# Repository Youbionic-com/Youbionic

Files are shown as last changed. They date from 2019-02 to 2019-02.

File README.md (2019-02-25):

## Youbionic

Youbionic! Youbionic

## Table of Contents
- [About Us](#about-us)
- [3d Model Assembly](#3d-model-assembly)
- [3d Printing](#3d-printing)
- [Actuators](#actuators)
- [Arduino Code](#arduino-code)
- [Youbionic Hand Handbook - Assembly Instructions](#handbook-assembly-instructions)
- [Technical Drawing](#technical-drawing)
- [Wiring Diagrams](#wiring-diagrams)

## About Us
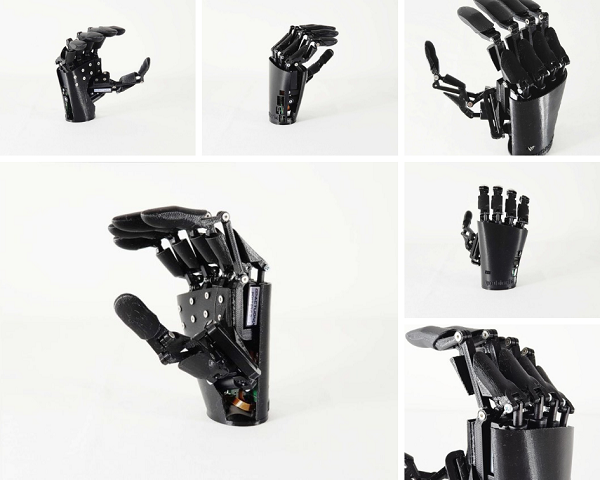
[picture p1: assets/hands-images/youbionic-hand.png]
Youbionic Hand! Youbionic Hand


<a href="http://www.youtube.com/watch?feature=player_embedded&v=_5nRUtHUUb4
" target="_blank">Youbionic Hand 2019</a>

To Understand more about Youbionic Hand, visit our webiste [youbionic.com](https://www.youbionic.com/)

### 3d Model Assembly
[Click here](assets/3d-model-assembly/Youbionic-Hand-2019-Assembly.igs) to find about our Youbionic Hand Assembly related information

### 3d Printing
Click on the below names to View 3D Printing Diagram

- [Back Smooth Logo Left](assets/3d-printing/Back_Smooth_logo_Left.stl) 
- [Back Smooth Logo Right](assets/3d-printing/Back_Smooth_logo_Right.stl)
- [Index Middle Ring](assets/3d-printing/Index-Middle-Ring.stl)
- [Palm Left](assets/3d-printing/Palm_Left.stl)
- [Palm Right](assets/3d-printing/Palm_Right.stl)
- [Rotation Thumb Left](assets/3d-printing/Rotation_Thumb_Left.stl)
- [Rotation Thumb Right](assets/3d-printing/Rotation_Thumb_Right.stl)
- [Thumb Pinkie](assets/3d-printing/Thumb-Pinkie.stl) 

### Actuators
<object data="assets/actuators/Actuonix-PQ12-Datasheet-D.pdf" type="application/pdf" width="700px" height="700px">
    <embed src="assets/actuators/Actuonix-PQ12-Datasheet-D.pdf">
        <p><a href="assets/actuators/Actuonix-PQ12-Datasheet-D.pdf">View PDF</a> to find more about Actuonix PQ12 Datasheet </p>
    </embed>
</object>

### Arduino Code
[Click here](assets/arduino-code/Youbionic_Hand.ino) to find about our Youbionic Hand

### Youbionic Hand Handbook - Assembly Instructions
<object data="assets/handbook-assembly-instructions/Youbionic-Hand-Handbook-Assembly-Instructions.pdf" type="application/pdf" width="700px" height="700px">
    <embed src="assets/handbook-assembly-instructions/Youbionic-Hand-Handbook-Assembly-Instructions.pdf">
        <p><a href="assets/handbook-assembly-instructions/Youbionic-Hand-Handbook-Assembly-Instructions.pdf">View PDF</a> to find more about our Youbionic Hand Handbook Assembly Instructions.</p>
    </embed>
</object>

### Technical Drawing
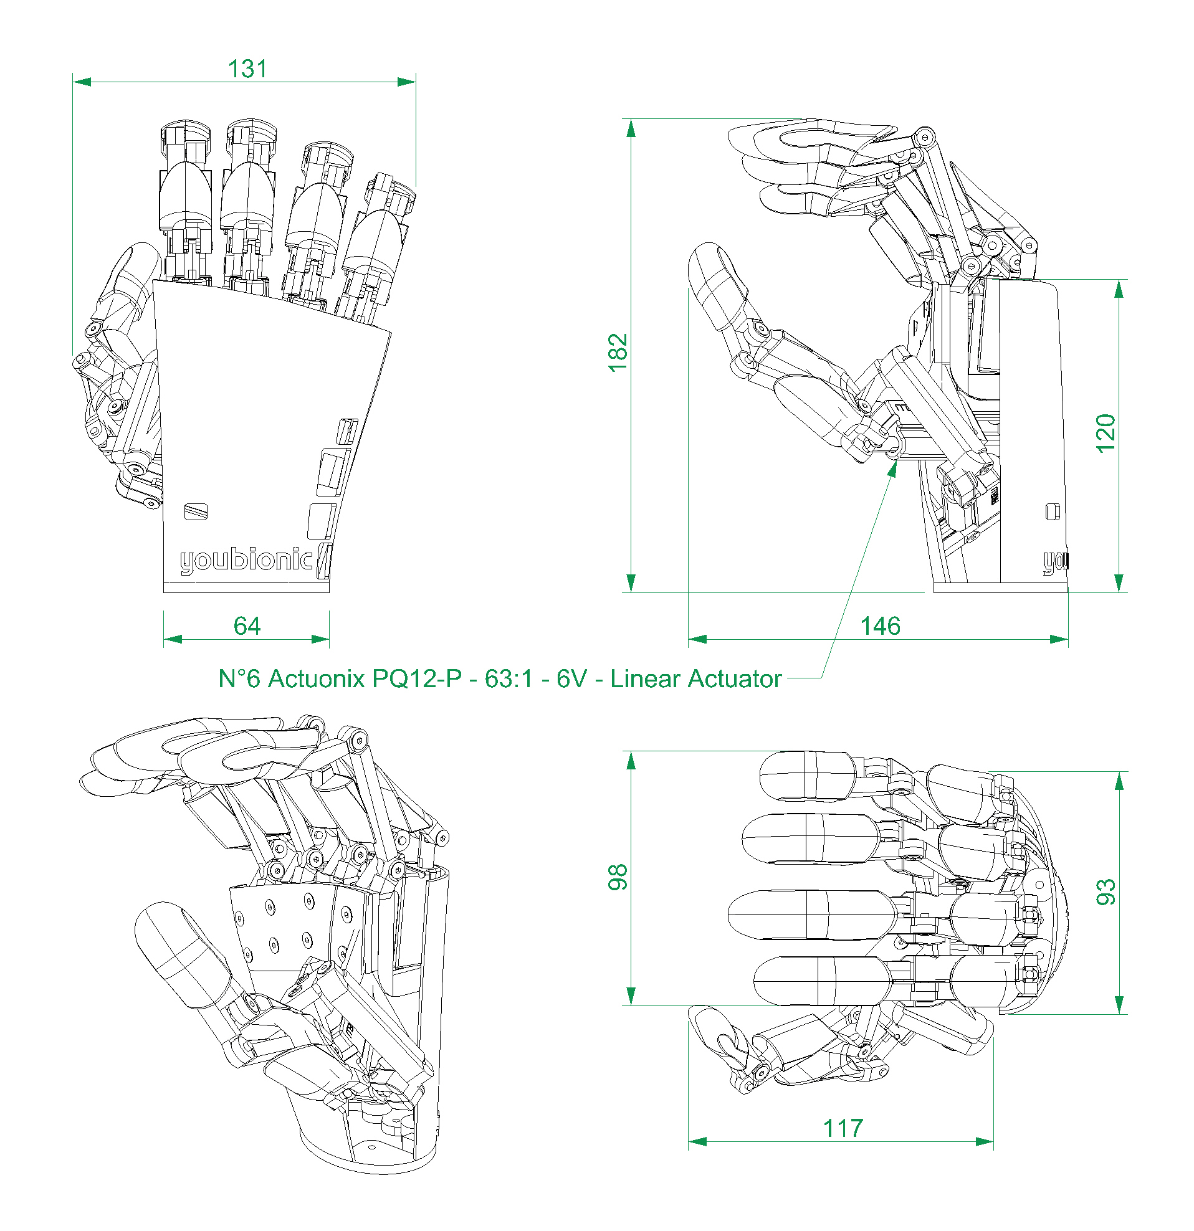
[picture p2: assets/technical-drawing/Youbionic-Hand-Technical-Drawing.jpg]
Technical Drawing! Technical Drawing


### Wiring Diagrams
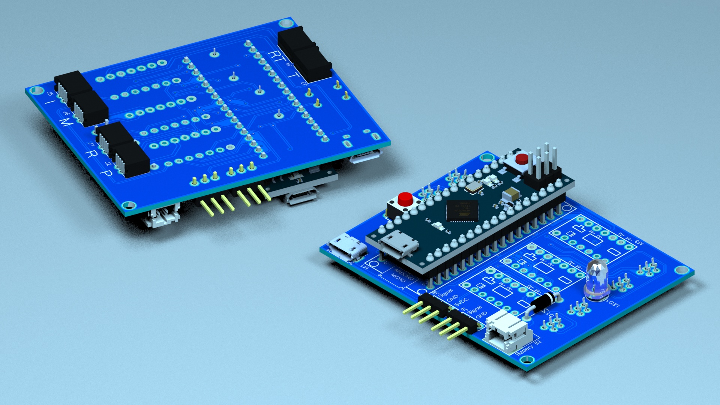
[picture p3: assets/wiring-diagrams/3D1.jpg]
Wiring Daigram! 3D


<object data="assets/wiring-diagrams/gerber-view.pdf" type="application/pdf" width="700px" height="700px">
    <embed src="assets/wiring-diagrams/gerber-view.pdf">
        <p><a href="assets/wiring-diagrams/gerber-view.pdf"> View PDF</a> to find more about our Gerber View.</p>
    </embed>
</object>

<object data="assets/wiring-diagrams/pcb-view.pdf" type="application/pdf" width="700px" height="700px">
    <embed src="assets/wiring-diagrams/pcb-view.pdf">
        <p><a href="assets/wiring-diagrams/pcb-view.pdf">View PDF</a> to find more about our PCB View.</p>
    </embed>
</object> 

<object data="assets/wiring-diagrams/schematic-v2.pdf" type="application/pdf" width="700px" height="700px">
    <embed src="assets/wiring-diagrams/schematic-v2.pdf">
        <p><a href="assets/wiring-diagrams/schematic-v2.pdf">View PDF</a> to find more about our Schematic View.</a></p>
    </embed>
</object>

## License

Released under [the MIT license](LICENSE).

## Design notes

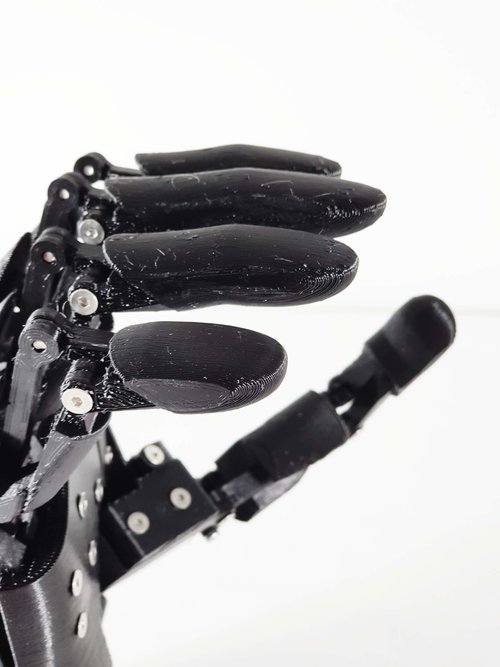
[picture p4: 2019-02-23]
assets/hands-images/8.HandSmooth.jpg

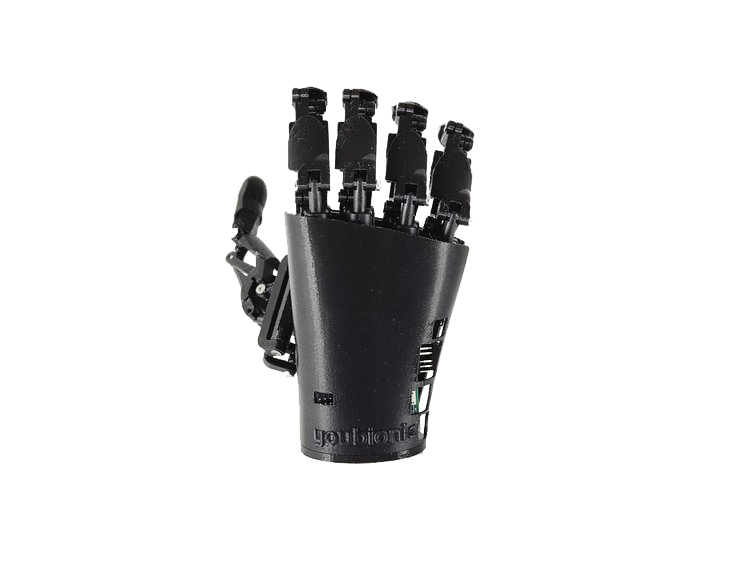
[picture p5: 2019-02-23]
assets/hands-images/5.HandSmooth.png

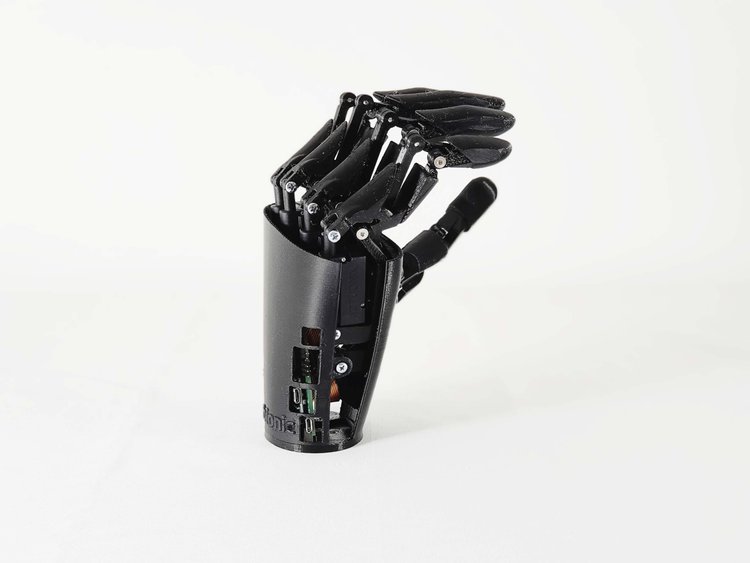
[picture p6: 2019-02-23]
assets/hands-images/3.HandSmooth.jpg

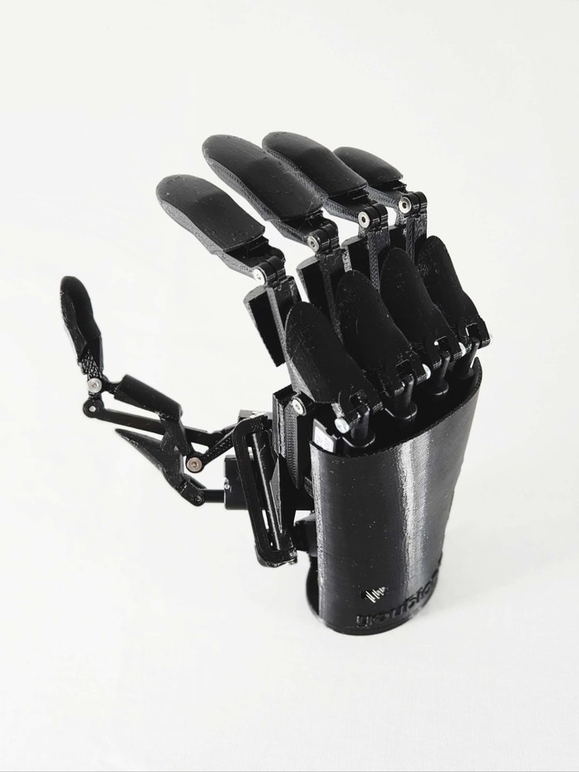
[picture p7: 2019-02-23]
assets/hands-images/4.HandSmooth.jpg

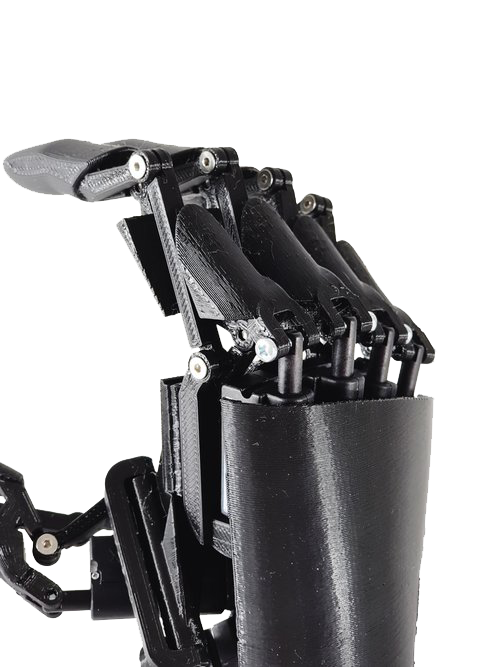
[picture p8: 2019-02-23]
assets/hands-images/6.HandSmooth.png

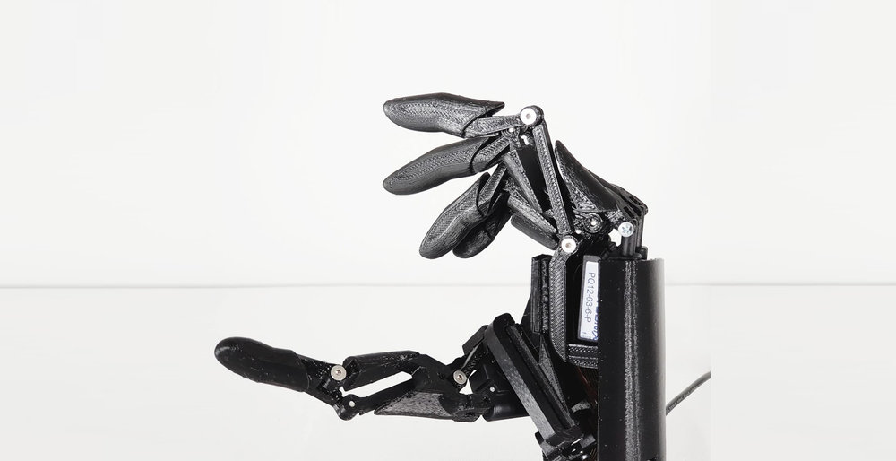
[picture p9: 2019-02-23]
assets/img/bg.jpg

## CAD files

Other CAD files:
assets/3d-model-assembly/Youbionic-Hand-2019-Assembly.igs
assets/3d-printing/Index-Middle-Ring.stl
assets/3d-printing/Rotation_Thumb_Left.stl
assets/3d-printing/Thumb-Pinkie.stl
assets/3d-printing/Rotation_Thumb_Right.stl
assets/3d-printing/Palm_Left.stl
assets/3d-printing/Back_Smooth_logo_Right.stl
assets/3d-printing/Back_Smooth_logo_Left.stl
assets/3d-printing/Palm_Right.stl

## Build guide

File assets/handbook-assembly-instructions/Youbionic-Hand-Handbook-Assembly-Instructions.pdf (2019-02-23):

# YOUBIONIC HAND

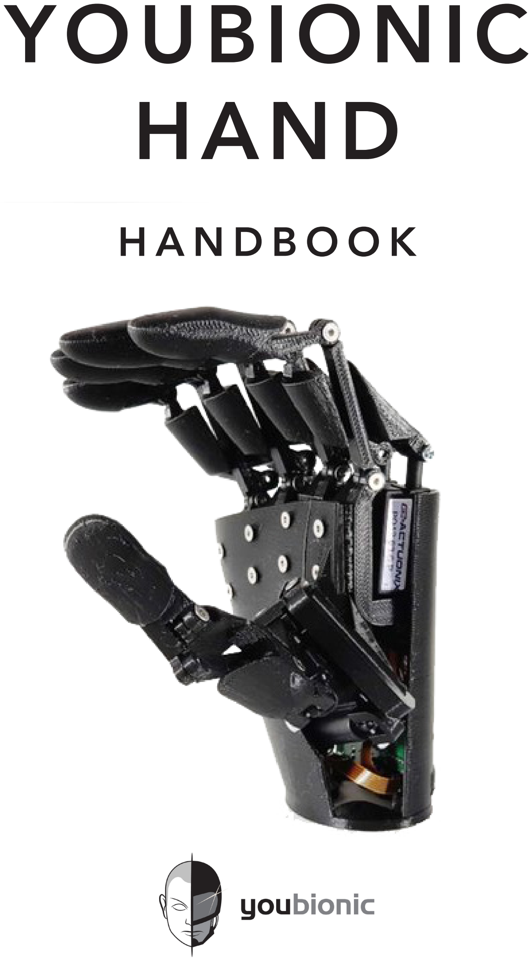
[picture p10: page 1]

# H A N D B O O K

## When 3d printing explodes in the world and printers spread, Youbionic provides the elements to create robotics and bionics never seen up to today. We can run to the future and

evolve as soon as possible.

# I N D E X

Bill of Material | 5
Assembly Istructions | 7

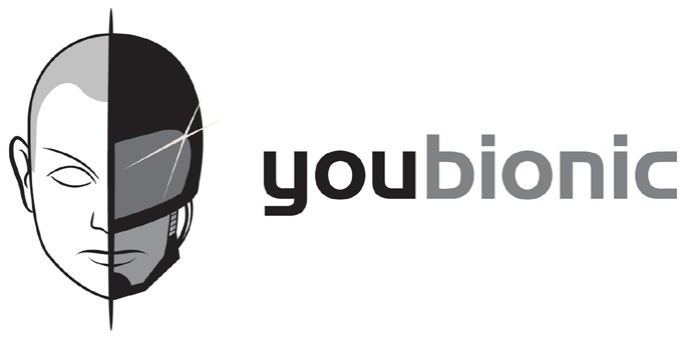
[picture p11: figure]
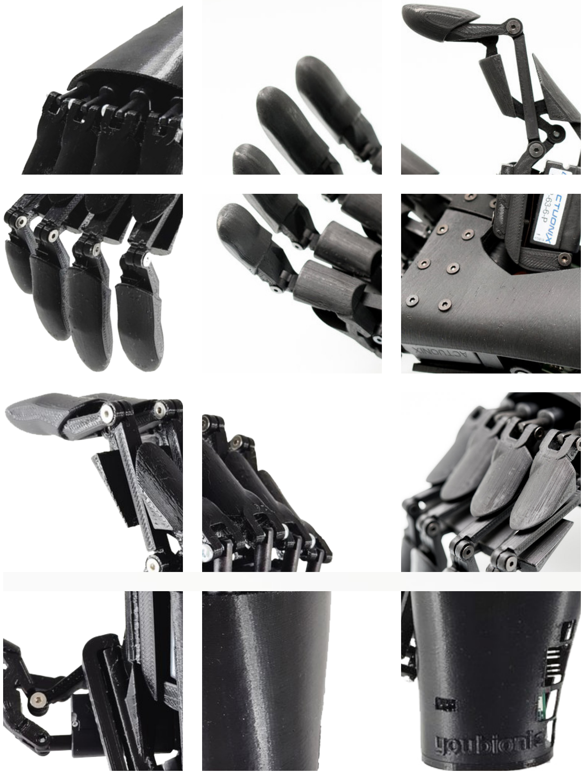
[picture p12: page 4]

# B I L L O F M A T E R I A L

N° 1 3D Hand prints
- Index
- Middle
- Ring
- Pinkie
- Thumb
- Rotation
- Palm
- Back

N° 1 Motherboard

N° 6 Actuators PQ12-P Linear Actuator - 63:1 - 6 vdc
To buy: https://www.actuonix.com/Actuonix-PQ-12-P-Linear-Actuator-p/pq12-p.htm

N° 1 Micro USB cable

N° 20 Screws M3x8 for finger assembly

N° 2 Screws M3x15 for Rotation System assembly

N° 10 Screws M3x15 for finger assembly on palm

N° 3 Screws M3x15 for Back assembly

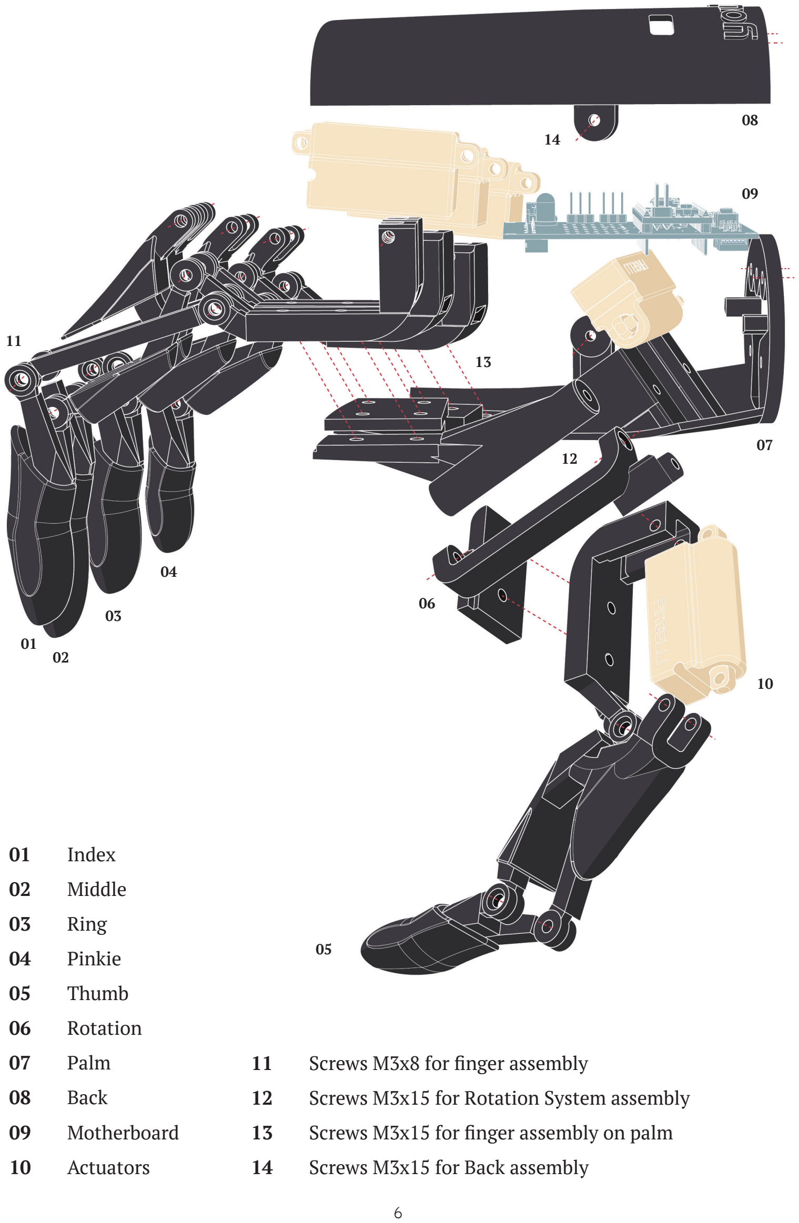
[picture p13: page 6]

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
### 01 Index 02 Middle 03 Ring 04 Pinkie 05 Thumb 06 Rotation 07 Palm 08 Back 09 Motherboard 10 Actuators

### 11 Screws M3x8 for finger assembly 12 Screws M3x15 for Rotation System assembly 13 Screws M3x15 for finger assembly on palm 14 Screws M3x15 for Back assembly

# A S S E M B L Y I N S T R U C T I O N S

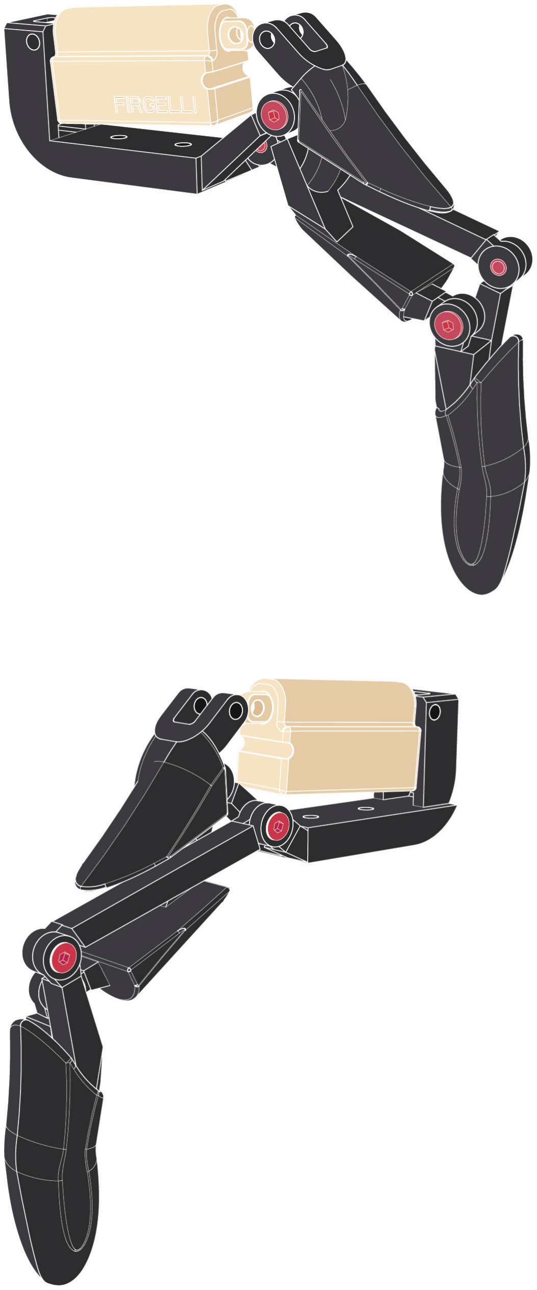
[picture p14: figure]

### 01 Finger assembly

Tighten the countersunk
screws M3x8 with a hexagon socket to assembly the fingers.

Don’t screw the screws all the way down, let the pieces rotate (make sure that the pieces can rotate, but leave a slight friction).

Proceed in this way for all the fingers.

N° 20 screws M3x8
(N° 4 screws for each finger)

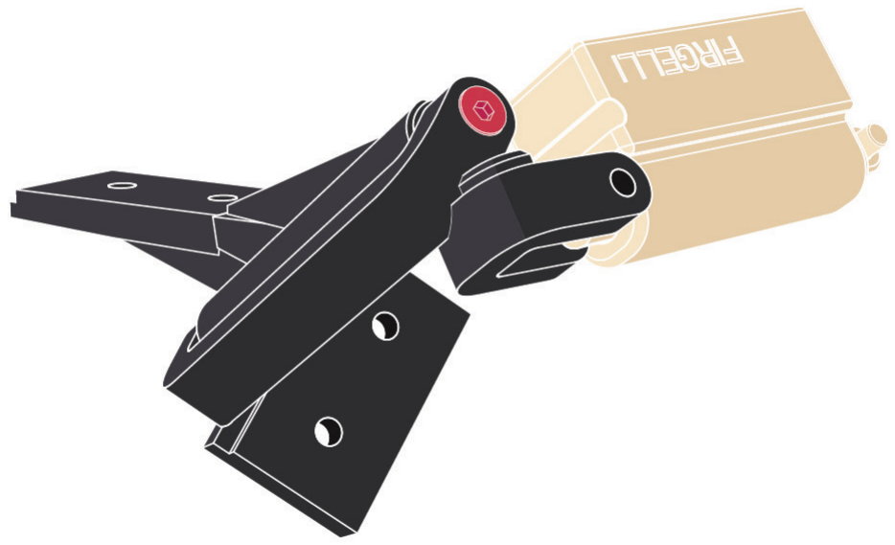
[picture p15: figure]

### 02 Rotation assembly

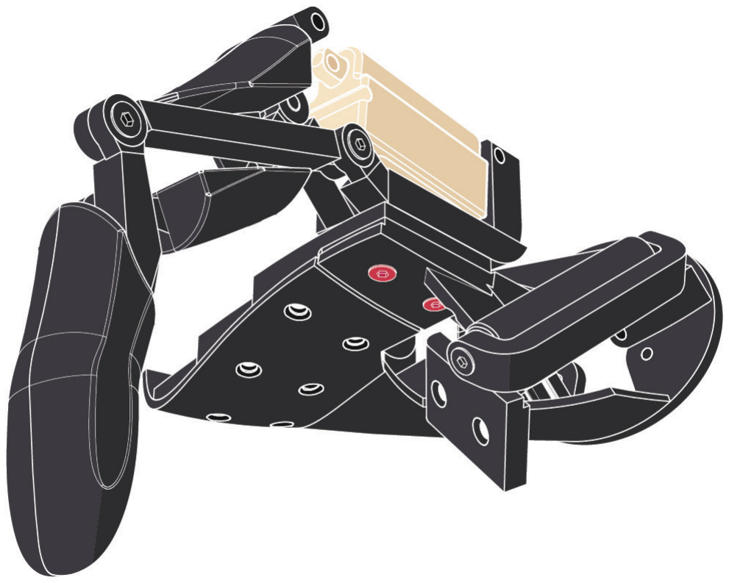
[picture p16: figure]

### 03 Palm assembly

Tighten the countersunk
screws M3x15 with a hexagon socket to assembly the rotation system.

Don’t screw the screws all the way down, let the pieces rotate (make sure that the pieces can rotate, but leave a slight friction).

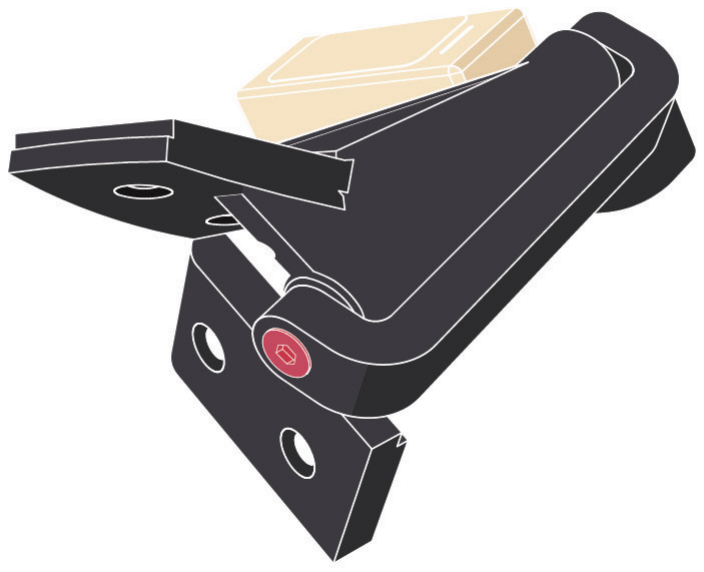
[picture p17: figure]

N° 2 screws M3x15

Tighten the countersunk
screws M3x15 with a hexagon socket to assembly fingers to palm.

To fix the fingers to the
palm, go all the way to the bottom with the head of the screw without tightening it any more because the screw threading will damage the
hole in the palm.

N° 10 screws M3x15
(N° 2 screws for each finger)

### 04 Back assembly

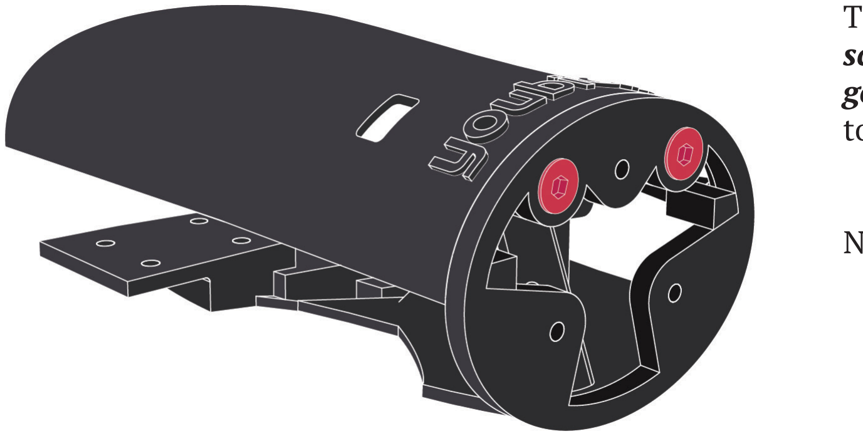
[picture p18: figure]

Tighten the countersunk
screws M3x15 with a hexagon socket to assembly back to hand and forearm.

N° 3 screws M3x15

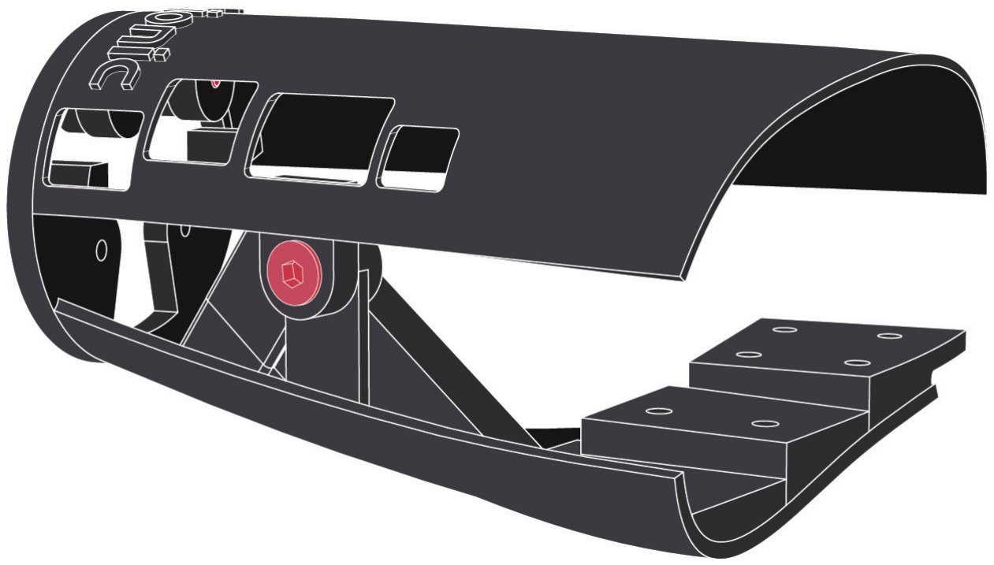
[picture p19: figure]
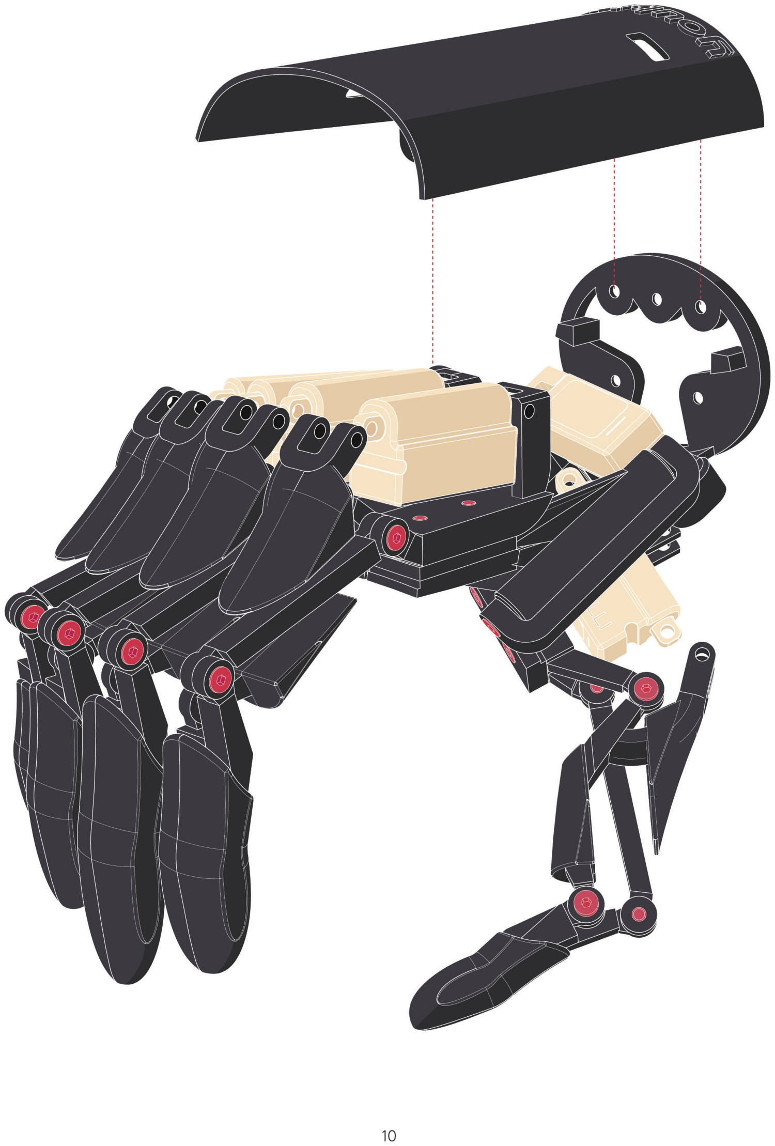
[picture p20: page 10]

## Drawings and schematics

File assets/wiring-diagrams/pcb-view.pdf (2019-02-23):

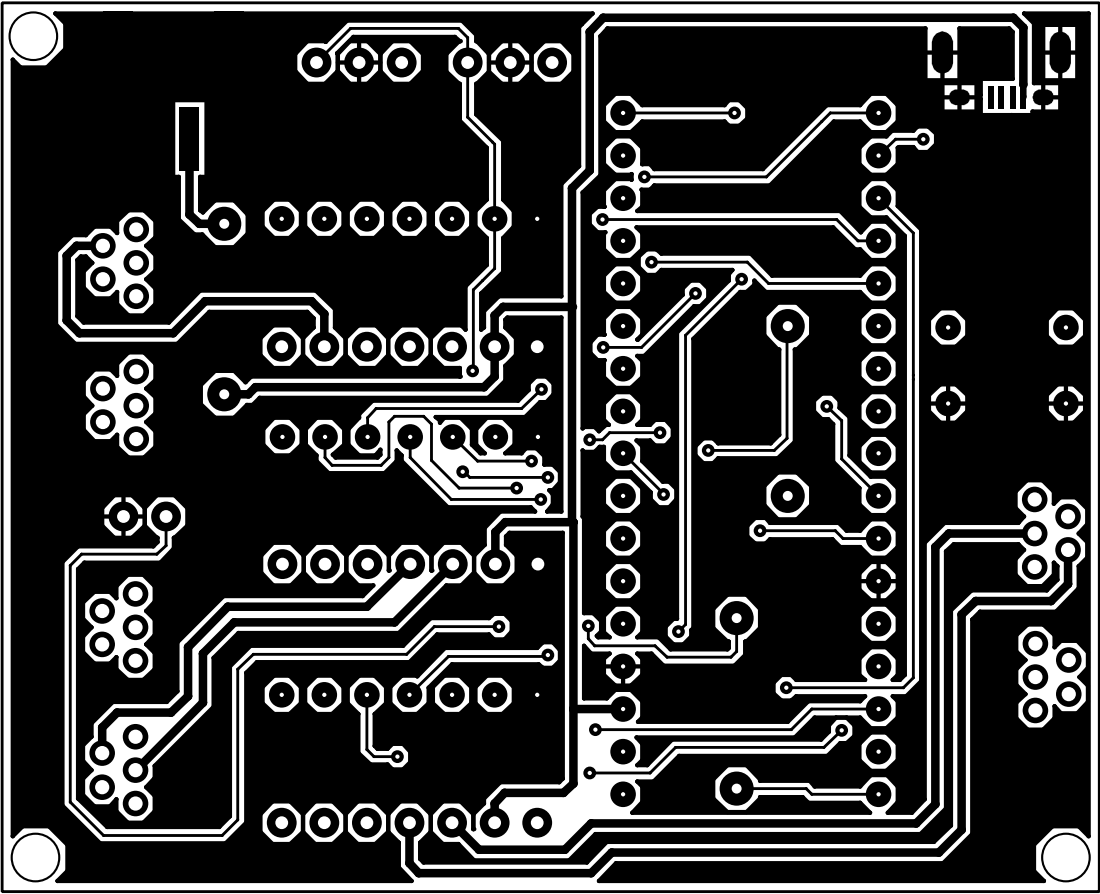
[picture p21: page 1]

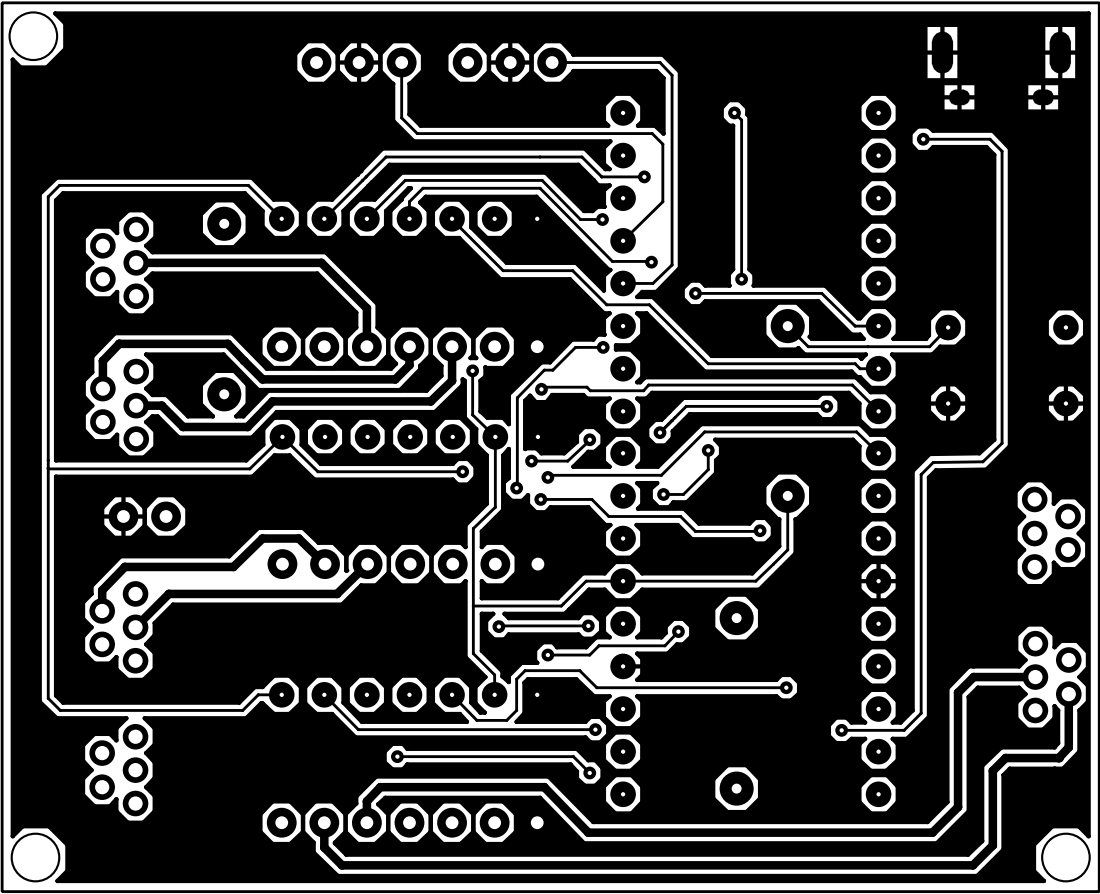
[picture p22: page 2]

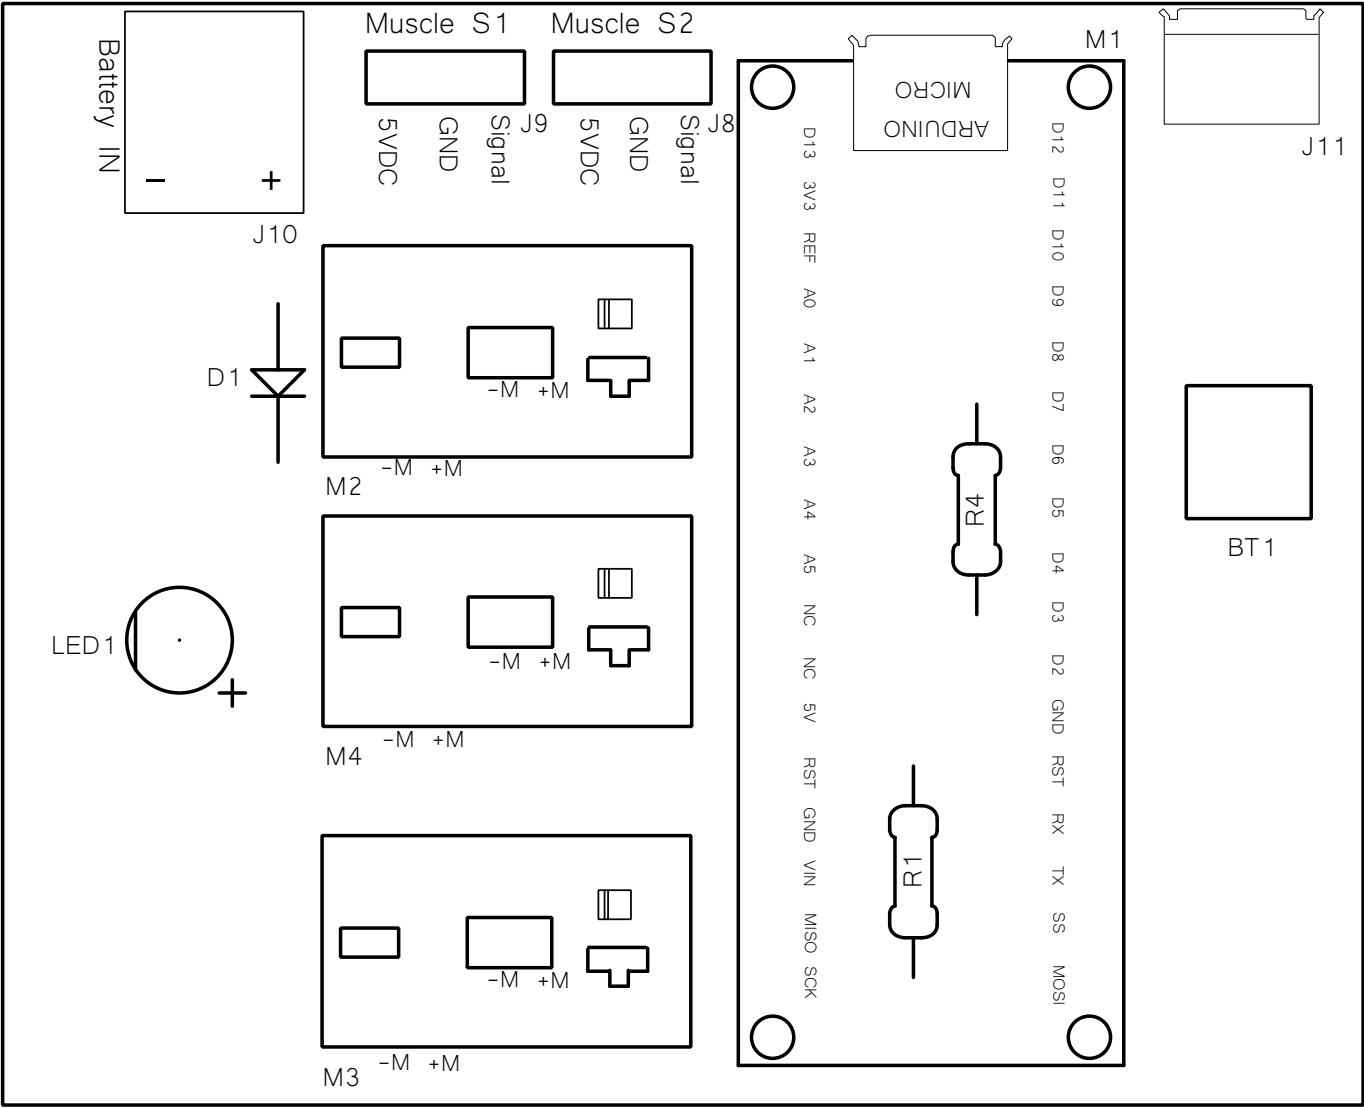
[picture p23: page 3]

ONI UDRA TX RX RST GND D2 D3 D4 D5 D6 D7 D8 D9 D10 D11 D12 VIN GND RST 5V NC NC A5 A4 A3 A2 A1 A0 REF 3V3 D13 MOSI SS SCK MISO M1 ORCI M M4M2 M3 J10 - + BMuscle S1 attery IN LED1 J9 J8 BT1 R4 R1 D1 5VDC GND Signal 5VDC GND Signal Muscle S2 J11 - M + M - M + M - M + M - M + M - M + M - M + M

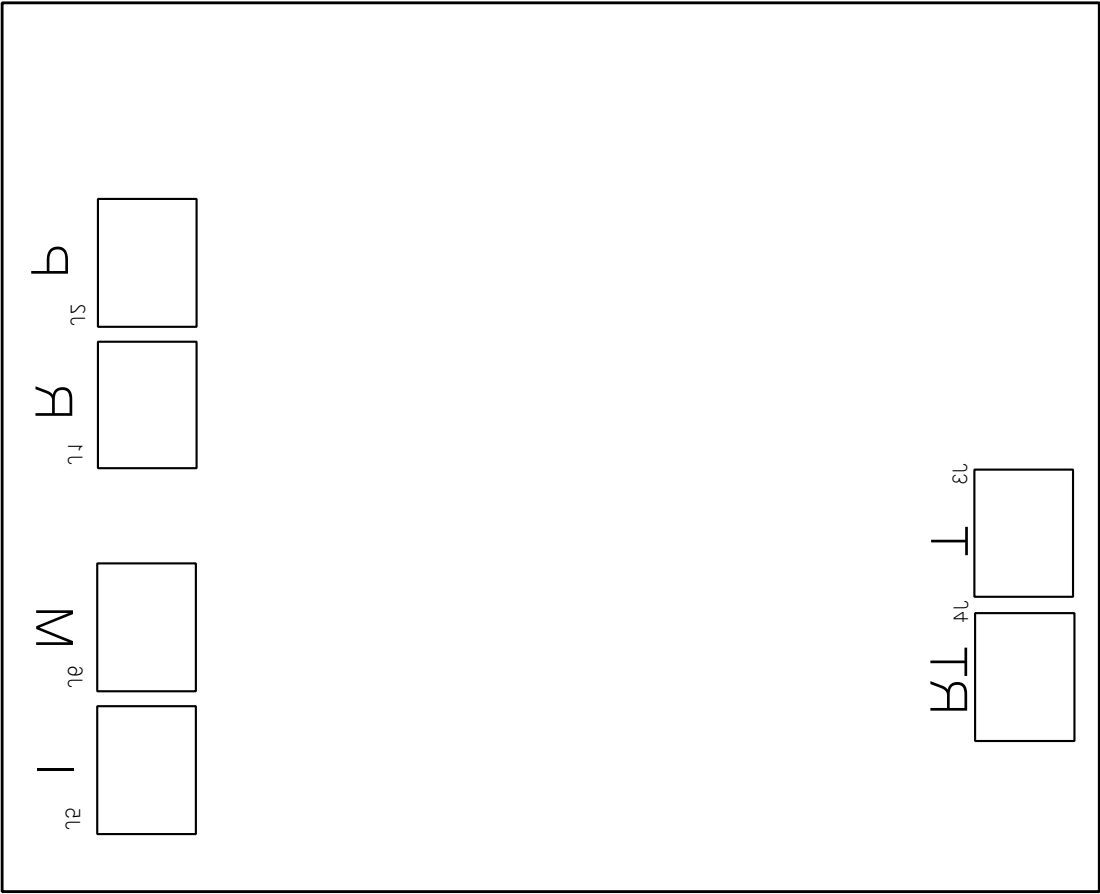
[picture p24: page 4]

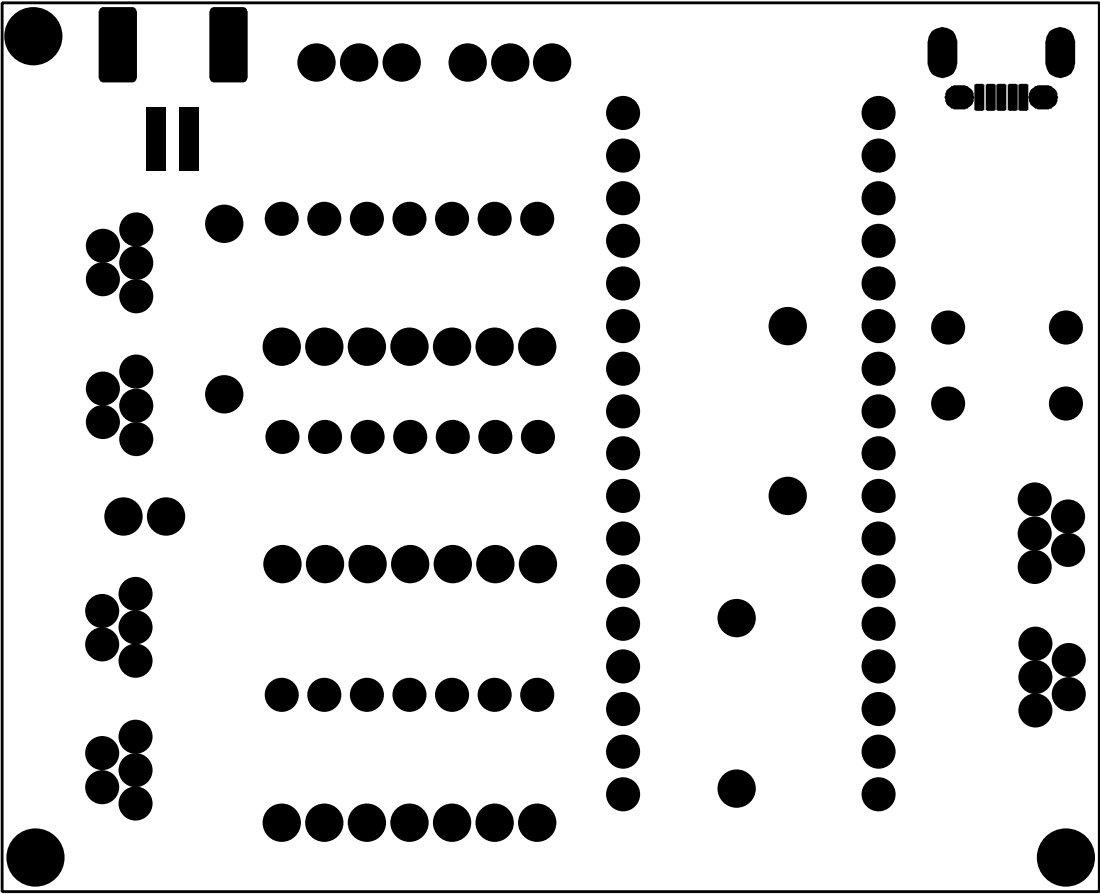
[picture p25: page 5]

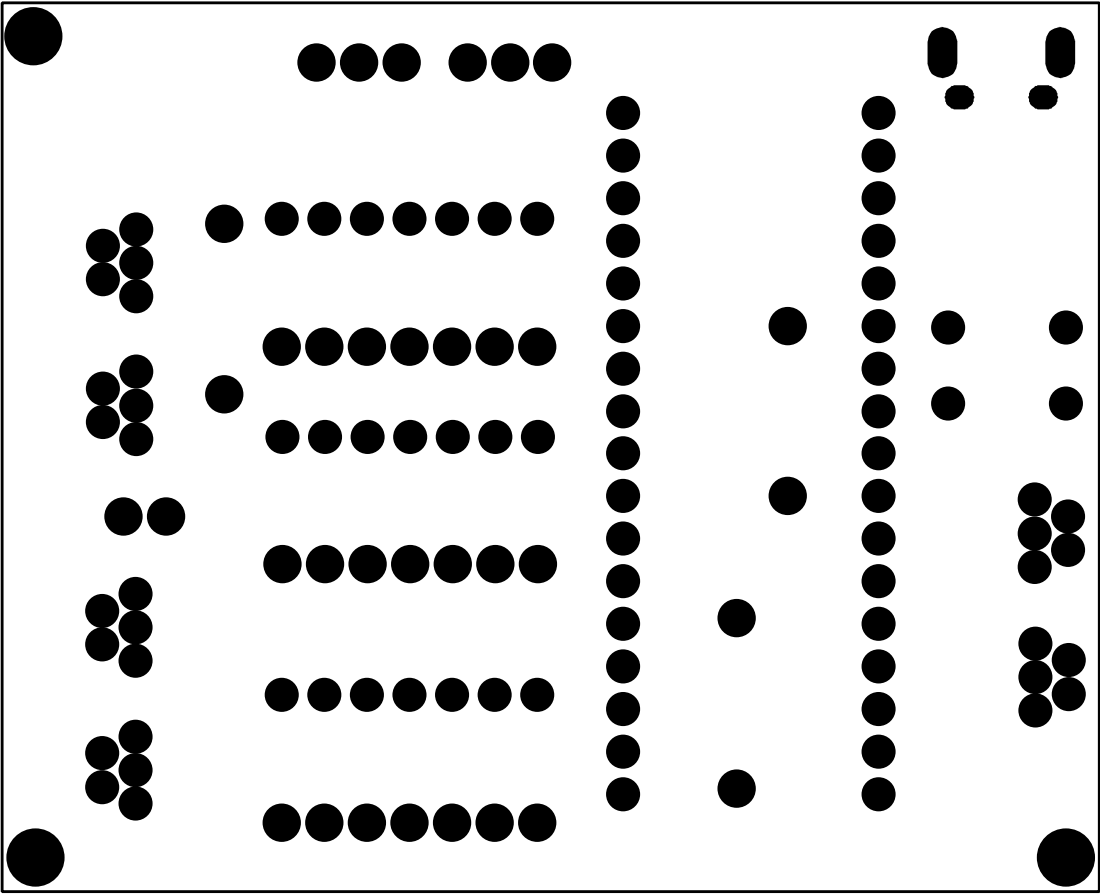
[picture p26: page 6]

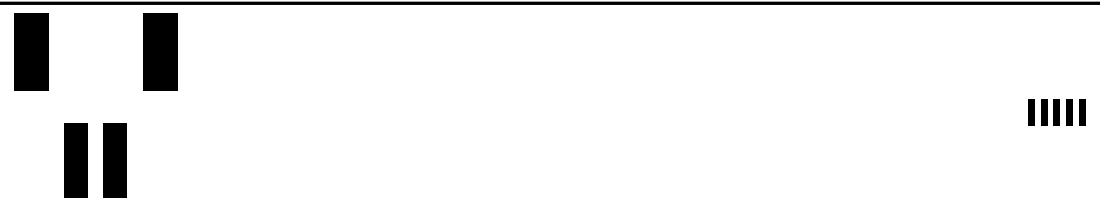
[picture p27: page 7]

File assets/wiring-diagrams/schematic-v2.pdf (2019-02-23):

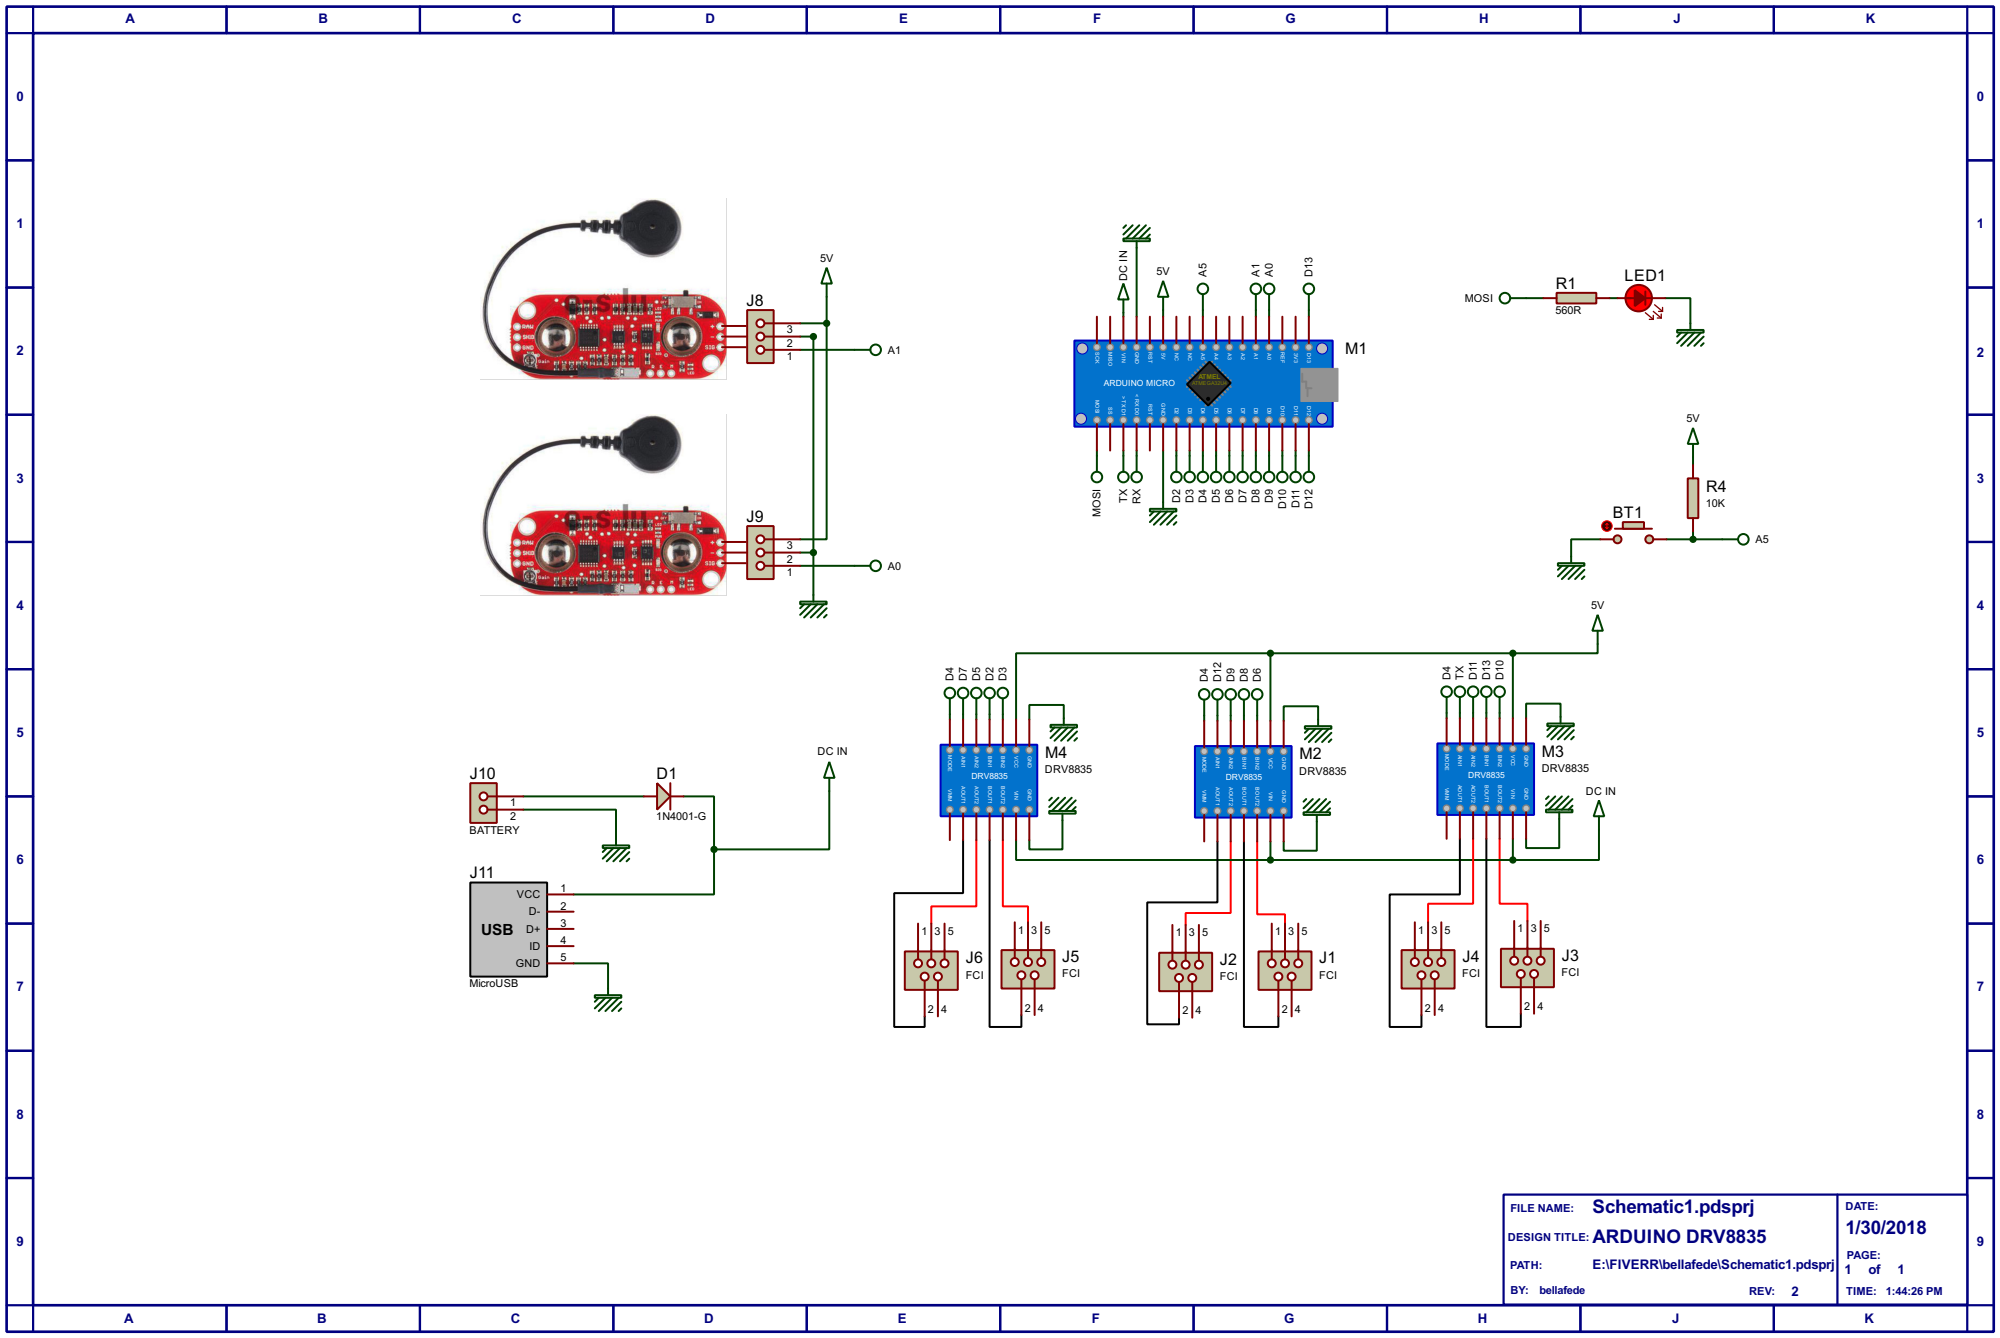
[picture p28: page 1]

SCK MISO SS MOSI

< RX D0 > TX D1 VIN GND

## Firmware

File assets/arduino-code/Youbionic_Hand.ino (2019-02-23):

#define pinMusSen A1

int position = 1;
int contractionlimitvalue= 150;
int instantreading = 0;
int savedreading = 0;
int maxcontractionset = 0;
int mincontractionset= 1023;
int minmaxdifferenceset = 0 ;

int maxcontraction = 0;
int mincontraction= 1023;
int deltavalue = 0;
int maxmindifference = 0 ;
int contractiontype = 1;

// A = Index
// B = Middle
// C = Ring
// D = Pinky
// E = Thumb
// F = Thumb rotation

int pinDirA = 2;
int pinPwmA = 3;
int pinDirB = 7;
int pinPwmB = 5;
int pinDirC = 8;
int pinPwmC = 6;
int pinDirD = 12;
int pinPwmD = 9;
int pinDirE = 13;
int pinPwmE = 10;
int pinDirF = 1;
int pinPwmF = 11;

int pinModeHigh = 4;

void setup() {

Serial.begin(9600);

pinMode ( pinDirA, OUTPUT );
pinMode ( pinPwmA, OUTPUT );

pinMode ( pinDirB, OUTPUT );
pinMode ( pinPwmB, OUTPUT );

pinMode ( pinDirC, OUTPUT );
pinMode ( pinPwmC, OUTPUT );

pinMode ( pinDirD, OUTPUT );
pinMode ( pinPwmD, OUTPUT );

pinMode ( pinDirE, OUTPUT );
pinMode ( pinPwmE, OUTPUT );

pinMode ( pinDirF, OUTPUT );
pinMode ( pinPwmF, OUTPUT );

pinMode ( pinModeHigh, OUTPUT );


digitalWrite( pinModeHigh,HIGH );

//Open the Hand
 digitalWrite( pinDirE,LOW );
 analogWrite( pinPwmE,255 );
 delay(200);
 digitalWrite( pinDirA,LOW );
 analogWrite( pinPwmA,255 );
 digitalWrite( pinDirB,LOW );
 analogWrite( pinPwmB,255 );
 digitalWrite( pinDirC,LOW );
 analogWrite( pinPwmC,255 );
 digitalWrite( pinDirD,LOW );
 analogWrite( pinPwmD,255 );
 digitalWrite( pinDirF,LOW );
 analogWrite( pinPwmF,255 );

delay(2000);

//Close the Hand
digitalWrite( pinDirD,HIGH );
analogWrite( pinPwmD,255 );
digitalWrite( pinDirC,HIGH );
analogWrite( pinPwmC,255 );
digitalWrite( pinDirB,HIGH );
analogWrite( pinPwmB,255 );
digitalWrite( pinDirA,HIGH );
analogWrite( pinPwmA,255 );
digitalWrite( pinDirE,HIGH );
analogWrite( pinPwmE,200 );

delay(2000);

//Open the Hand
 digitalWrite( pinDirE,LOW );
 analogWrite( pinPwmE,255 );
 delay(200);
 digitalWrite( pinDirA,LOW );
 analogWrite( pinPwmA,255 );
 digitalWrite( pinDirB,LOW );
 analogWrite( pinPwmB,255 );
 digitalWrite( pinDirC,LOW );
 analogWrite( pinPwmC,255 );
 digitalWrite( pinDirD,LOW );
 analogWrite( pinPwmD,255 );
 digitalWrite( pinDirF,LOW );
 analogWrite( pinPwmF,255 );

//Muscle Contraction Calibration Phase
delay(1000);     // Time to let the signal stabilize
instantreading = analogRead( pinMusSen );   //read the value of the contraction
savedreading = instantreading ;   //write into savedreading a number already read, different from zero
delay(25);
for (int i=0; i <= 400; i++)  // 10 seconds to perform accurate calibration
{
instantreading = analogRead( pinMusSen );
  if (instantreading > savedreading  &&  instantreading > maxcontractionset )
{
maxcontractionset = instantreading ;
}
  if (instantreading < savedreading  &&  instantreading < mincontractionset)
{
mincontractionset= instantreading ;
}
savedreading = instantreading;
Serial.print  ("Lettura Istantanea: ");
Serial.println( instantreading );
delay(25);
}

contractionlimitvalue= (( ( maxcontractionset - mincontractionset) / 2 ) + mincontractionset) * 0.8 ;

Serial.print  ("Maximum Contraction Set: ");
Serial.println(maxcontractionset);

Serial.print  ("Minimum Contrast Set: ");
Serial.println(mincontractionset);

// Stop Calibration Signed 
 digitalWrite( pinDirF,HIGH );
 analogWrite( pinPwmF,255 );

delay(500);

 digitalWrite( pinDirF,LOW );
 analogWrite( pinPwmF,255 );

delay(500);

 digitalWrite( pinDirF,LOW );
 analogWrite( pinPwmF,0 );

}



void loop() 
{
out:
instantreading = analogRead( pinMusSen );
if ( instantreading > contractionlimitvalue)
{
         savedreading = instantreading ;    //save savedreading different from zero
        maxcontraction = instantreading ;     //save maxcontraction different from zero
         mincontraction= instantreading ;         //save mincontraction different from zero
delay(25);
  for (int i=0; i <= 20; i++)   //   1/2 second to run the command
{
instantreading = analogRead( pinMusSen );
    if (instantreading > savedreading  &&  instantreading > maxcontraction )
  {
  maxcontraction = instantreading ;
  }
    if (instantreading < savedreading  &&  instantreading < mincontraction)
  {
  mincontraction= instantreading ;
  }
savedreading = instantreading;
Serial.print  ("Instant reading : ");
Serial.println( instantreading );
delay(25);
}
deltavalue = analogRead( pinMusSen );
maxmindifference = maxcontraction - mincontraction;
minmaxdifferenceset = maxcontractionset - mincontractionset;



if ( deltavalue < (contractionlimitvalue* 0.9) &&  mincontraction< (contractionlimitvalue* 0.8)  )
{
  contractiontype = 1 ;  //Contraction Pulse
  }
if ( deltavalue > (contractionlimitvalue* 0.9) &&  mincontraction> (contractionlimitvalue* 0.8)  )
{
  contractiontype = 2 ;  //Contraction Durable
  }
if ( deltavalue > (contractionlimitvalue* 0.9) &&  mincontraction< (contractionlimitvalue* 0.8)  )
{
  contractiontype = 3 ;
  }





if ( contractiontype == 2 && position == 1 ) 
  {
//Run to fist
fist:
digitalWrite( pinDirD,HIGH );
analogWrite( pinPwmD,255 );
digitalWrite( pinDirC,HIGH );
analogWrite( pinPwmC,255 );
digitalWrite( pinDirB,HIGH );
analogWrite( pinPwmB,255 );
digitalWrite( pinDirA,HIGH );
analogWrite( pinPwmA,255 );
digitalWrite( pinDirE,HIGH );
analogWrite( pinPwmE,200 );

delay(100);

instantreading = analogRead( pinMusSen );
if ( instantreading > contractionlimitvalue)
{
//than continue to Run to fist
goto fist ;
}

delay(100);

instantreading = analogRead( pinMusSen );
if ( instantreading > contractionlimitvalue)
{
//than continue to Run to fist
goto fist ;
}

delay(100);

instantreading = analogRead( pinMusSen );
if ( instantreading > contractionlimitvalue)
{
//than continue to Run to fist
goto fist ;
}

//otherwise stop the motors
digitalWrite( pinDirD,HIGH );
analogWrite( pinPwmD,0 );
digitalWrite( pinDirC,HIGH );
analogWrite( pinPwmC,0 );
digitalWrite( pinDirB,HIGH );
analogWrite( pinPwmB,0 );
digitalWrite( pinDirA,HIGH );
analogWrite( pinPwmA,0 );
digitalWrite( pinDirE,HIGH );
analogWrite( pinPwmE,0 );

delay(150);

Serial.print  ("Contraction type : ");
Serial.println( contractiontype );

Serial.println  ("Close Hand ");

position = 2 ;
contractiontype = 0;
goto out ;

}

if ( contractiontype == 2 && position == 2 ) 
  {
//Run to fist
fist2:
digitalWrite( pinDirD,HIGH );
analogWrite( pinPwmD,255 );
digitalWrite( pinDirC,HIGH );
analogWrite( pinPwmC,255 );
digitalWrite( pinDirB,HIGH );
analogWrite( pinPwmB,255 );
digitalWrite( pinDirA,HIGH );
analogWrite( pinPwmA,255 );
digitalWrite( pinDirE,HIGH );
analogWrite( pinPwmE,200 );

delay(100);

instantreading = analogRead( pinMusSen );
if ( instantreading > contractionlimitvalue)
{
//than continue to Run to fist
goto fist2 ;
}

delay(100);

instantreading = analogRead( pinMusSen );
if ( instantreading > contractionlimitvalue)
{
//than continue to Run to fist
goto fist2 ;
}

delay(100);

instantreading = analogRead( pinMusSen );
if ( instantreading > contractionlimitvalue)
{
//than continue to Run to fist
goto fist2 ;
}

//otherwise stop the motors
digitalWrite( pinDirD,HIGH );
analogWrite( pinPwmD,0 );
digitalWrite( pinDirC,HIGH );
analogWrite( pinPwmC,0 );
digitalWrite( pinDirB,HIGH );
analogWrite( pinPwmB,0 );
digitalWrite( pinDirA,HIGH );
analogWrite( pinPwmA,0 );
digitalWrite( pinDirE,HIGH );
analogWrite( pinPwmE,0 );

delay(150);

Serial.print  ("Contraction type : ");
Serial.println( contractiontype );

Serial.println  ("Close Hand ");

position = 2 ;
contractiontype = 0;
goto out ;

}

if ( contractiontype == 1 && position == 2 )
  {
// Open the Hand
 digitalWrite( pinDirE,LOW );
 analogWrite( pinPwmE,255 );
 delay(200);
 digitalWrite( pinDirA,LOW );
 analogWrite( pinPwmA,255 );
 digitalWrite( pinDirB,LOW );
 analogWrite( pinPwmB,255 );
 digitalWrite( pinDirC,LOW );
 analogWrite( pinPwmC,255 );
 digitalWrite( pinDirD,LOW );
 analogWrite( pinPwmD,255 );
 digitalWrite( pinDirF,LOW );
 analogWrite( pinPwmF,255 );

Serial.print  ("Contraction type : ");
Serial.println( contractiontype );

Serial.println  ("Open Hand ");


delay(1200);

position = 1 ;
contractiontype = 0;
goto out ;


}

if ( contractiontype == 1 && position == 1 )
  {
// get the 3 Fingers position (Position 3)
digitalWrite( pinDirB,HIGH );
analogWrite( pinPwmB,0 );
digitalWrite( pinDirA,HIGH );
analogWrite( pinPwmA,0 );
digitalWrite( pinDirE,HIGH );
analogWrite( pinPwmE,0 );
digitalWrite( pinDirF,HIGH );
analogWrite( pinPwmF,0 );

digitalWrite( pinDirD,HIGH );
analogWrite( pinPwmD,255 );
digitalWrite( pinDirC,HIGH );
analogWrite( pinPwmC,255 );

position = 3 ;
contractiontype = 0;
goto out ;

}

if ( contractiontype == 2 && position == 3 ) 
  {
//Run to 3 Fingers closed
TFC:  // 3 Fingers Closed

digitalWrite( pinDirB,HIGH );
analogWrite( pinPwmB,255 );
digitalWrite( pinDirA,HIGH );
analogWrite( pinPwmA,255 );
digitalWrite( pinDirE,HIGH );
analogWrite( pinPwmE,255 );

delay(100);

instantreading = analogRead( pinMusSen );
if ( instantreading > contractionlimitvalue)
{
//than continue to 3 Fingers closed
goto TFC ;
}

delay(100);

instantreading = analogRead( pinMusSen );
if ( instantreading > contractionlimitvalue)
{
//than continue to 3 Fingers closed
goto TFC ;
}

delay(100);

instantreading = analogRead( pinMusSen );
if ( instantreading > contractionlimitvalue)
{
//than continue to 3 Fingers closed
goto TFC ;
}

//otherwise stop the motors
digitalWrite( pinDirD,HIGH );
analogWrite( pinPwmD,0 );
digitalWrite( pinDirC,HIGH );
analogWrite( pinPwmC,0 );
digitalWrite( pinDirB,HIGH );
analogWrite( pinPwmB,0 );
digitalWrite( pinDirA,HIGH );
analogWrite( pinPwmA,0 );
digitalWrite( pinDirE,HIGH );
analogWrite( pinPwmE,0 );

delay(150);

position = 4 ;
contractiontype = 0;
goto out ;

}

if ( contractiontype == 2 && position == 4 ) 
  {
//Run to 3 Fingers closed
TFCC:  // 3 Fingers Closed

digitalWrite( pinDirB,HIGH );
analogWrite( pinPwmB,255 );
digitalWrite( pinDirA,HIGH );
analogWrite( pinPwmA,255 );
digitalWrite( pinDirE,HIGH );
analogWrite( pinPwmE,235 );

delay(100);

instantreading = analogRead( pinMusSen );
if ( instantreading > contractionlimitvalue)
{
//than continue to 3 Fingers closed
goto TFCC ;
}

delay(100);

instantreading = analogRead( pinMusSen );
if ( instantreading > contractionlimitvalue)
{
//than continue to 3 Fingers closed
goto TFCC ;
}

delay(100);

instantreading = analogRead( pinMusSen );
if ( instantreading > contractionlimitvalue)
{
//than continue to 3 Fingers closed
goto TFCC ;
}

//otherwise stop the motors
digitalWrite( pinDirD,HIGH );
analogWrite( pinPwmD,0 );
digitalWrite( pinDirC,HIGH );
analogWrite( pinPwmC,0 );
digitalWrite( pinDirB,HIGH );
analogWrite( pinPwmB,0 );
digitalWrite( pinDirA,HIGH );
analogWrite( pinPwmA,0 );
digitalWrite( pinDirE,HIGH );
analogWrite( pinPwmE,0 );

delay(150);

position = 4 ;
contractiontype = 0;
goto out ;

}

if ( contractiontype == 1 && position == 4 )
  {
// Open the Hand
 digitalWrite( pinDirE,LOW );
 analogWrite( pinPwmE,255 );
 delay(200);
 digitalWrite( pinDirA,LOW );
 analogWrite( pinPwmA,255 );
 digitalWrite( pinDirB,LOW );
 analogWrite( pinPwmB,255 );
 digitalWrite( pinDirC,LOW );
 analogWrite( pinPwmC,255 );
 digitalWrite( pinDirD,LOW );
 analogWrite( pinPwmD,255 );
 digitalWrite( pinDirF,LOW );
 analogWrite( pinPwmF,255 );

Serial.print  ("Contraction type : ");
Serial.println( contractiontype );

Serial.println  ("Open Hand ");


delay(1200);

position = 1 ;
contractiontype = 0;
goto out ;


}

if ( contractiontype == 1 && position == 3 )
  {
// get the 1 Fingers position (Position 5)

digitalWrite( pinDirA,HIGH );
analogWrite( pinPwmA,0 );
digitalWrite( pinDirE,HIGH );
analogWrite( pinPwmE,0 );
digitalWrite( pinDirF,HIGH );
analogWrite( pinPwmF,0 );
digitalWrite( pinDirD,HIGH );
analogWrite( pinPwmD,0 );
digitalWrite( pinDirC,HIGH );
analogWrite( pinPwmC,0 );

digitalWrite( pinDirB,HIGH );
analogWrite( pinPwmB,255 );

position = 5 ;
contractiontype = 0;
goto out ;

}
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

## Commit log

2019-02-23 adding igs file
    [Youbionic-Hand-2019-Assembly.igs]
2019-02-23 adding stl files
    [Back_Smooth_logo_Left.stl, Back_Smooth_logo_Right.stl, Palm_Left.stl, Palm_Right.stl]
